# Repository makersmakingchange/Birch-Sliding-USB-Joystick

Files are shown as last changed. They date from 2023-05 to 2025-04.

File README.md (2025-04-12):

# Birch Sliding USB Joystick
The Birch Sliding USB Joystick is a small, proportional joystick that has a sliding motion and can be used for adaptive gaming. It has a small range of motion of ±2mm and requires approximately 115 grams-force to fully deflect. It is low profile, with a height of 2.4 mm with the standard topper. This joystick has interchangable toppers and optional mount adapters. The Birch Sliding USB Joystick has the same joystick mechanism as the Aspen Sliding Joystick, but is the USB version.

The Birch Sliding USB Joystick has a cable with a USB-A connector. It acts as a USB HID gamepad with a single joystick and is compatible with a variety of devices including PC and the USB ports of the Microsoft Xbox Adaptive Controller. The deadzone can be adjusted through a serial interface.

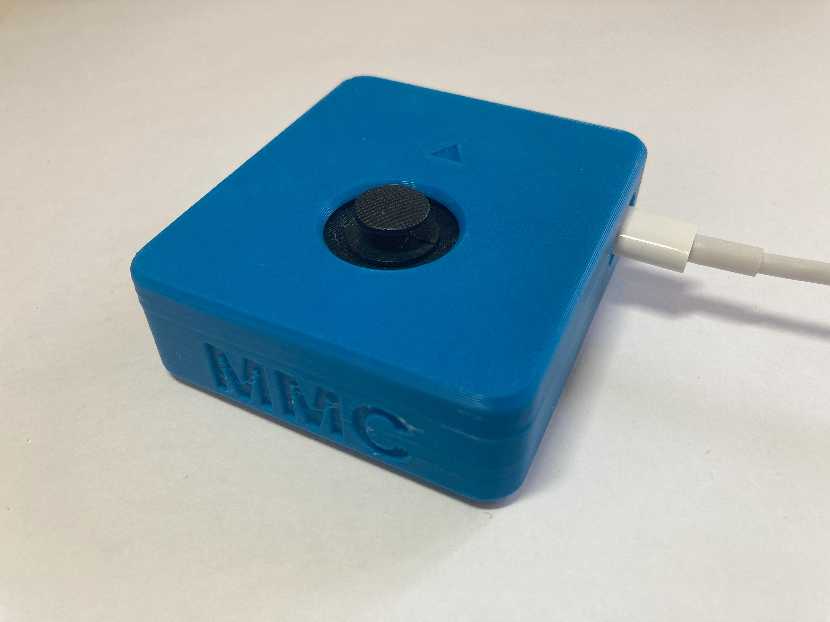
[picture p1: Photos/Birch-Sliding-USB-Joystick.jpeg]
Picture of the Birch Sliding USB Joystick, it is blue and small with MMC written on the side and an arrow on top.


## More info at
- [Makers Making Change Assistive Device Library Listing](https://www.makersmakingchange.com/s/product/birch-sliding-usb-joystick/01tJR0000009357YAA)

## OpenAT Joysticks
This design is part of the [OpenAT Joystick Project](https://github.com/makersmakingchange/OpenAT-Joysticks), a collection of open source designs for digital access and adapted gaming.  

## How to Obtain a Birch Sliding USB Joystick
### 1. Do it Yourself (DIY) or Do it Together (DIT)

This is an open-source assistive technology, so anyone is free to build it. All of the files and instructions required to build the Birch Sliding USB Joystick are contained within this repository. Refer to the Maker Guide below.

### 2. Request a build of this device

If you would like to obtain a Birch Sliding USB Joystick , you may submit a build request through the [MMC Library Page](https://www.makersmakingchange.com/s/product/birch-sliding-usb-joystick/01tJR0000009357YAA). The requestor is responsible for the cost of materials and any shipping.

### 3. How to build this device for someone else

If you have the skills and equipment to build this device, and would like to donate your time to create the switch for someone who needs it, visit the [MMC Maker Wanted](https://makersmakingchange.com/maker-wanted/) section.

## Getting Started

### 1. Verify Joystick Type
The Birch Sliding USB Joystick is a USB joystick that emulates an HID gamepad allowing use either directly with a PC or with the Microsoft Xbox Adaptive Controller (XAC). Verify that this is the type of joystick the user would like. 

If they want an analog joystick with the same sliding motion instead, they should be directed to the [Aspen Sliding Joystick](https://github.com/makersmakingchange/Aspen-Sliding-Joystick). Note: the Aspen Sliding Joystick is compatible with the Sony Access Controller, but the Birch Sliding USB Joystick is not. 

<!---
Other available joysticks can be found through the [Joystick Selection Guide](https://makersmakingchange.com/resource/analog-joystick-selection-guide/)
--->

### 2. Read through the Maker Guide

The [Maker Guide](/Documentation/Birch_Joystick_Maker_Guide.pdf) contains all the neccessary information to build the device.

### 3. Read the Makers Checklist

Use the Makers Checklist in the [Maker Guide](/Documentation/Birch_Joystick_Maker_Guide.pdf) to confirm details and customization options with the user.

### 4. Order the Off-The-Shelf Components

The [Bill of Materials](/Documentation/Birch_Joystick_BOM.csv) lists all of the parts and components required to build the Birch Sliding USB Joystick. 

### 5. Print the 3D Printable components

Print the components needed for the Birch Sliding USB Joystick. Make sure to ask the user if they would like any of the optional prints such as toppers or mount adapters.

All of the files and individual print files can be in the [/Build_Files/3D_Print_Files](/Build_Files/3D_Print_Files/) folder.

### 6. Assemble the Aspen Sliding Joystick

Reference the Assembly Guide section in the [Maker Guide](/Documentation/Birch_Joystick_Maker_Guide.pdf) for the tools and steps required to build the device.

## Files
### Documentation
| Document             | Version | Link | 
|----------------------|---------|------------------------------------------------------------------------------------------|
| Design Rationale     | 1.0     | [Birch_Joystick_Design_Rationale](/Documentation/Birch_Joystick_Design_Rationale.pdf)    | 
| Maker Guide          | 1.0     | [Birch_Joystick_Maker_Guide](/Documentation/Birch_Joystick_Maker_Guide.pdf)     	        | 
| Bill of Materials    | 1.0     | [Birch_Joystick_Bill_of_Materials](/Documentation/Birch_Joystick_BOM.csv)     		    | 
| User Guide           | 1.0     | [Birch_Joystick_User_Guide](/Documentation/Birch_Joystick_User_Guide.pdf)    	    |
| Changelog            | 1.0     | [CHANGES](/CHANGES.txt)     			| 

### Design Files
 - [CAD Files](/Design_Files)

### Build Files
 - [3D Printing Files](/Build_Files/3D_Print_Files)
 - [Firmware](/Build_Files/Software/OpenAT_Joystick_Software_Birch)

## License

Everything needed or used to design, make, test, or prepare the Birch Mini Joystick is licensed under the CERN 2.0 Weakly Reciprocal license <https://ohwr.org/project/cernohl/wikis/Documents/CERN-OHL-version-2> (CERN-OHL-W).

Accompanying material such as instruction manuals, videos, and other copyrightable works that are useful but not necessary to design, make, test, or prepare the Oak Compact Joystick are published under a Creative Commons Attribution-ShareAlike 4.0 license <https://creativecommons.org/licenses/by-sa/4.0/> (CC BY-SA 4.0).

## Attribution

Contributors 
- Josie Versloot, Neil Squire. Hardware and enclosure design, coding, documentation. 
- Tyler Fentie, Neil Squire. Hardware and enclosure design. 
- Milad Hajihassan, Neil Squire. Coding.

The joystick software utilizes the [Adafruit TinyUSB Library for Arduino](https://github.com/adafruit/Adafruit_TinyUSB_Arduino) which is made available under an [MIT license](https://github.com/adafruit/Adafruit_TinyUSB_Arduino/blob/master/LICENSE).

The documentation template was created by Makers Making Change / Neil Squire and is used under a CC BY-SA 4.0 license. It is available at the following link: https://github.com/makersmakingchange/OpenAT-Template

----

<!-- ABOUT MMC START -->
## About Makers Making Change
[Makers Making Change Logo](https://www.makersmakingchange.com/)

Makers Making Change is a program of [Neil Squire](https://www.neilsquire.ca/), a Canadian non-profit that uses technology, knowledge, and passion to empower people with disabilities.

Makers Making Change leverages the capacity of community based Makers, Disability Professionals and Volunteers to develop and deliver affordable Open Source Assistive Technologies.

 - Website: [www.MakersMakingChange.com](https://www.makersmakingchange.com/)
 - GitHub: [makersmakingchange](https://github.com/makersmakingchange)
 - Bluesky: [@makersmakingchange.bsky.social](https://bsky.app/profile/makersmakingchange.bsky.social)
 - Instagram: [@makersmakingchange](https://www.instagram.com/makersmakingchange)
 - Facebook: [makersmakechange](https://www.facebook.com/makersmakechange)
 - LinkedIn: [Neil Squire Society](https://www.linkedin.com/company/neil-squire-society/)
 - Thingiverse: [makersmakingchange](https://www.thingiverse.com/makersmakingchange/about)
 - Printables: [MakersMakingChange](https://www.printables.com/@MakersMakingChange)

### Contact Us
For technical questions, to get involved, or to share your experience we encourage you to [visit our website](https://www.makersmakingchange.com/) or [contact us](https://www.makersmakingchange.com/s/contact).
<!-- ABOUT MMC END -->

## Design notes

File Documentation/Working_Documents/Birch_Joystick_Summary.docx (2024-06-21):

This document is intended to be a summary of a device to make it easier to add to the website.

# Product Information

## Product Name

Birch Sliding USB Joystick

## Device Category

Mark any relevant categories with an “X”:

| Adapted Toys
| Aids for Daily Living (ADL)
| Assistive Switches
| Communication Aids (AAC)
X | Computer Access
| Environmental Controls
X | Gaming
| Keyguard
| Kits
| LipSyncs
| Mounting
X | Recreation and Leisure
| Seating and Positioning
| Switch Interfaces
| Writing Aids

## User Value Statement

If you're looking for a USB joystick with a very small range of motion we'd like to point you to the Birch Sliding USB Joystick.

## Designer

Makers Making Change

# Device Info

## Overview

The Birch Sliding USB Joystick is a small USB joystick that moves in a sliding motion instead of the typical pivoting motion of a joystick or thumbstick. It can be used for adapted gaming, either with the Xbox Adaptive Controller (https://www.xbox.com/en-CA/accessories/controllers/xbox-adaptive-controller) or used directly with PC.

The PSP-style game controller sliding thumbstick joystick has a range of motion of ±2 mm and requires approximately 115 grams-force to fully deflect. A range of toppers are available for this joystick.

## Disability Type

Select one or more disability types and mark with an “X”:

X | Agility / Dexterity
| Arthritis
| Cognitive
| Hearing
| Mobility
| Mobility
| Pain
X | SCI
| Vision
| Other

## Disability Type Description

## For joystick users who require a joystick with a very small range of motion for gaming.

## How To Use

To use the Birch Sliding USB Joystick, first position the joystick for the user, mounting if needed. Then, plug in the USB-C to USB-A cable to both the joystick and the host device, such as the Xbox Adaptive Controller. Wait for the joystick to initialize, then move the joystick like a thumbstick on a standard controller.

For full instructions, please refer to the User Guide. <link>

## Estimated Cost

The estimated material cost of the device for a single build:

| $0 - $10
X | $11 - $25
| $26 - $50
| $51 - $100
| $101 - $250
| $250+

## Attribution

Designed by Neil Squire Society / Makers Making Change

Contributors

- Josie Versloot, Neil Squire. Hardware and enclosure design, coding, documentation.
- Tyler Fentie, Neil Squire. Hardware and enclosure design.
- Milad Hajihassan, Neil Squire. Coding.

The software utilizes the Adafruit TinyUSB Library for Arduino (https://github.com/adafruit/Adafruit_TinyUSB_Arduino) which is made available under an MIT license (https://github.com/adafruit/Adafruit_TinyUSB_Arduino/blob/master/LICENSE).

The documentation template was created by Makers Making Change / Neil Squire and is used under a CC BY-SA 4.0 license. It is available at the following link: https://github.com/makersmakingchange/OpenAT-Template

# Maker Info

## Project Skills

Mark the required project skills with an “X”:

X | 3D Printing
| Custom PCB
X | Electronics
| Laser Cutting
| Mechanics
X | Software
X | Soldering
| Woodworking
| Other

## Skills Description

## This is an intermediate build requiring electronics, mechanics, 3D printing, and using the Arduino IDE.

## Tools Needed

X | 3D Printer
X | Common Hand Tools
| Common Power Tools
| Laser Cutter
X | Soldering Iron
| Specialized Tooling

## Print time (hrs)

4.0

## Assembly time (hrs)

1.0

## Build Instructions

This build consists of a number of off-the-shelf electronic components that are soldered into a protoboard and connected together using wires and solder bridges. The electronics are then assembled into a 3D printed enclosure and the firmware is flashed to the microcontroller using the Arduino IDE.

Detailed step-by-step instructions are available in the Maker Guide <link>.

## Download Link

<Link to direct download of all project files e.g., Github Zip folder>

## Project Link

< Link to GitHub repository>

# License

## License

This repository describes Open Hardware:

- Everything needed or used to design, make, test, or prepare the Birch Sliding USB Joystick is licensed under the CERN 2.0 Weakly Reciprocal license (CERN-OHL-W v2) or later (https://cern.ch/cern-ohl) .
- All software is under the GNU General Public License v3.0 (GPL-3.0) (https://www.gnu.org/licenses/gpl.html).
- Accompanying material such as instruction manuals, videos, and other copyrightable works that are useful but not necessary to design, make, test, or prepare the Birch Sliding USB Joystick are published under a Creative Commons Attribution-ShareAlike 4.0 license (CC BY-SA 4.0) (https://creativecommons.org/licenses/by-sa/4.0/) .

You may redistribute and modify this documentation and make products using it under the terms of the CERN-OHL-W v2 (https://cern.ch/cern-ohl). This documentation is distributed WITHOUT ANY EXPRESS OR IMPLIED WARRANTY, INCLUDING OF MERCHANTABILITY, SATISFACTORY QUALITY AND FITNESS FOR A PARTICULAR PURPOSE. Please see the CERN-OHL-W v2 for applicable conditions.

© 2022 by <Author>. This work is licensed under the CC BY SA 4.0 License: http://creativecommons.org/licenses/by-sa/4.0 Page 1 of 2

V1.0 | MAY 2024 Birch Sliding USB Joystick Summary

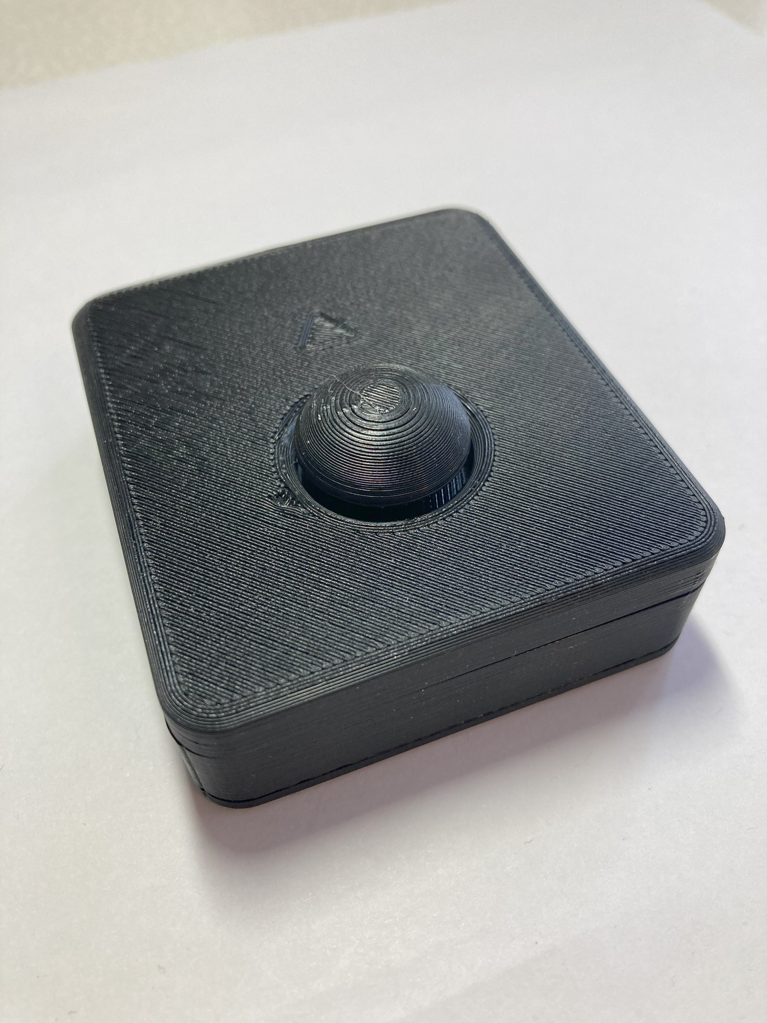
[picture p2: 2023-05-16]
Photos/Birch-Joystick-Medium-Dome-Topper.jpeg

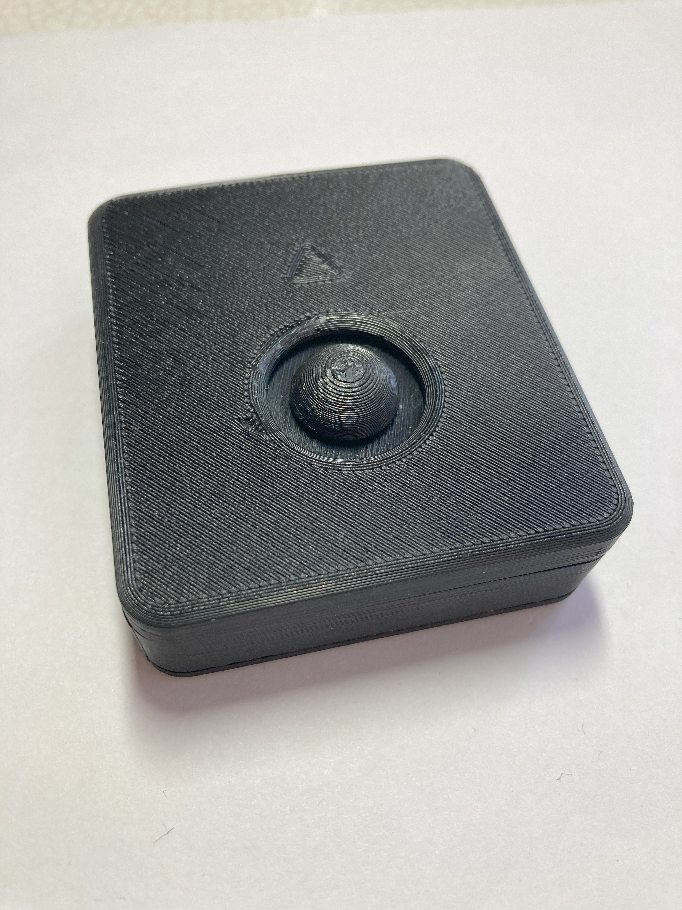
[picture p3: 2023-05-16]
Photos/Birch-Joystick-Small-Dome-Topper.jpeg

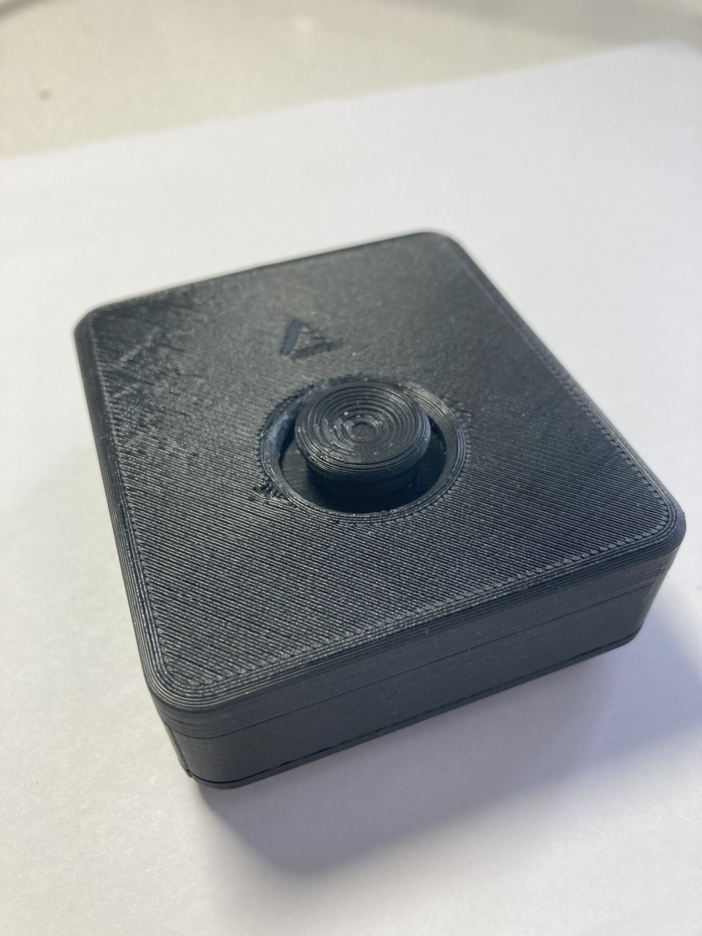
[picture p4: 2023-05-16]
Photos/Birch-Joystick-Concave-Topper.jpeg

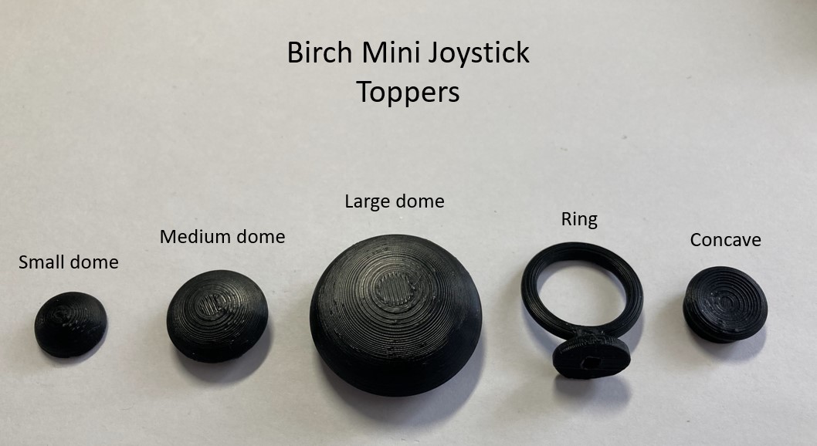
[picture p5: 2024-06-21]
Photos/Birch-Joystick-Toppers-Labelled.jpeg

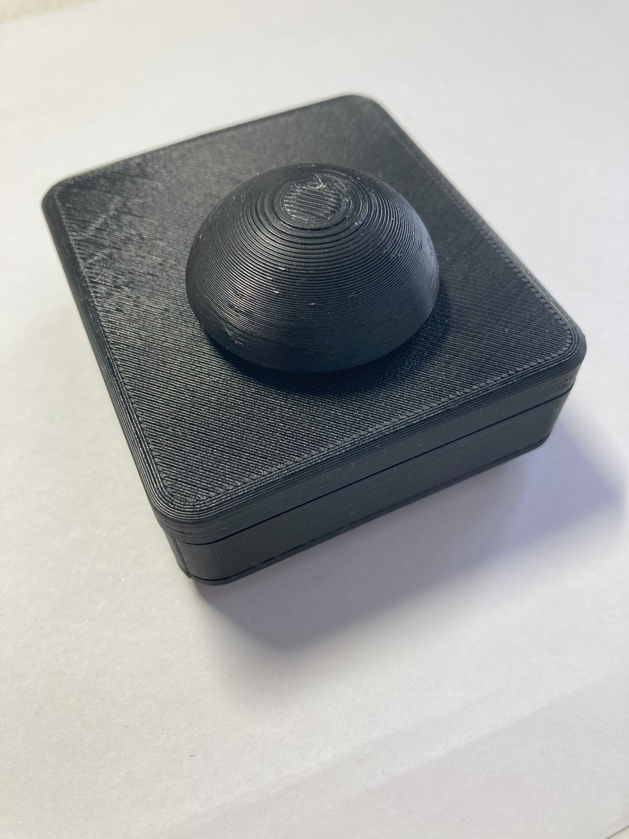
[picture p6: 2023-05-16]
Photos/Birch-Joystick-Large-Dome-Topper.jpeg

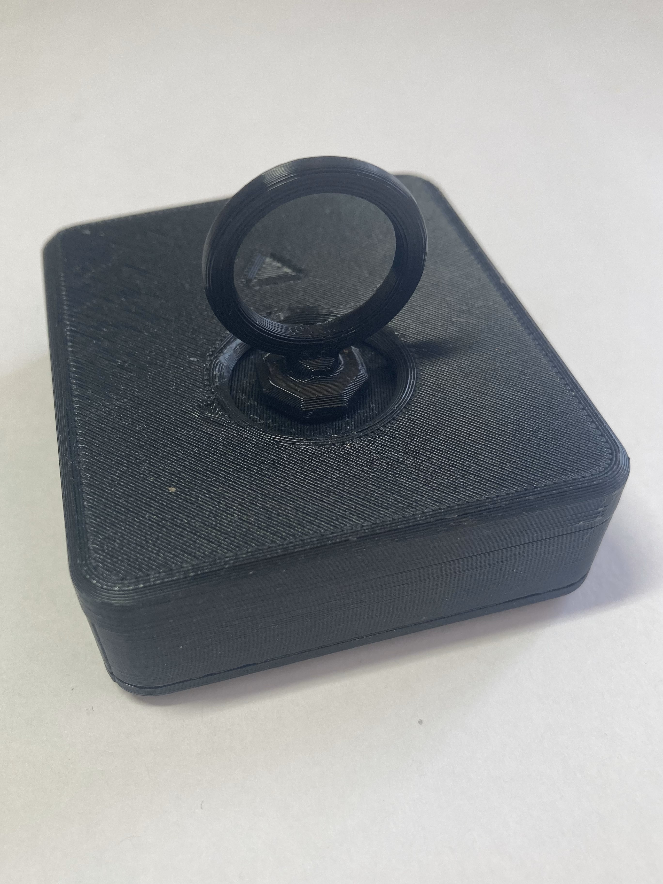
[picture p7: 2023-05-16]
Photos/Birch-Joystick-Ring-Topper.jpeg

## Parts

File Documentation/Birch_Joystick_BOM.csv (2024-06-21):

Birch Sliding USB Joystick |  |  |  |  |  |  |  | Unit Cost | Total Cost | Total Print time (hr) | Total filament (g)
Version: V1.0 |  | Last Updated: 2024-June-18 |  |  |  |  |  | $27.50 | $42.80 | 3.65 | 46.1
Commercial Parts
ID | Part Name | Part Type | QTY | QTY/PKG | $/PKG | PKG QTY | $/Unit | Extended | Total | Link
 | Mini 2-Axis Analog Thumbstick | Electrical | 1 | 1 | $3.87 | 1 | $3.87 | $3.87 | $3.87 | https://www.digikey.ca/en/products/detail/adafruit-industries-llc/2765/6193582
 | Analog Mini Thumbstick Breakout Board | Electrical | 1 | 1 | $2.18 | 1 | $2.18 | $2.18 | $2.18 | https://www.digikey.ca/en/products/detail/adafruit-industries-llc/3246/6193594
 | Universal Proto-board PCB 4cm x 6cm | Electrical | 1 | 3 | $3.63 | 1 | $1.21 | $1.21 | $3.63 | https://www.digikey.ca/en/products/detail/adafruit-industries-llc/4785/13617529
 | SeeedStudio XAIO RP2040 | Electrical | 1 | 1 | $6.80 | 1 | $6.80 | $6.80 | $6.80 | https://www.digikey.ca/en/products/detail/seeed-technology-co-ltd/102010428/14672129
 | 24 AWG Wire, 1 foot | Electrical | 1 | 1 | $0.80 | 1 | $0.80 | $0.80 | $0.80 | https://www.digikey.ca/en/products/detail/cnc-tech/1007-24-1-2000-007-1-TD/17799170
 | M2 x 6 mm Self Tapping Screws | Mechanical | 8 | 1000 | $12.99 | 1 | $0.01 | $0.10 | $12.99 | https://a.co/d/1mQQYbU
 | USB C cable - 6 ft | Electrical | 1 | 1 | $3.28 | 1 | $3.28 | $3.28 | $3.28 | https://www.digikey.ca/en/products/detail/cvilux-usa/DH-20M50053/13177348
 | M3 hex nut x2 | Mechanical | 2 | 1 | $0.28 | 2 | $0.28 | $0.56 | $0.56 | https://www.digikey.ca/en/products/detail/keystone-electronics/4708/4499301
 | (Optional for mount) M3x12mm screw x2 | Mechanical | 0 | 1 | $1.11 | 0 | $1.11 | $- | $- | https://www.digikey.ca/en/products/detail/apm-hexseal/RM3X12MM-2701/2063201
 | (Optional for mount) Tee nut | Mechanical | 0 | 1 | $0.48 | 0 | $0.48 | $- | $- | https://www.homedepot.ca/product/paulin-1-4-inch-20-tee-nuts-4-prong-5-16-inch-barrel-length/1000129429
 | Digikey shipping (if spending less than $100) | Shipping | 1 | 1 | $8.00 | 1 | $8.00 | $8.00 | $8.00
3D Printed Parts ESTIMATED PRICING USING 1KG ROLL COST: |  | $25.00
ID | Part | Material | QTY | Mass (g) / Unit | Time / Unit |  | Print Time (Min) | Estimated Unit Price | Total Price | Link
 | Birch_Enclosure_Bottom | PLA | 1 | 14.9 | 127 |  | 127 | $0.37 | $0.37
 | Birch_Enclosure_Top | PLA | 1 | 10.6 | 74 |  | 74 | $0.27 | $0.27
 | Inner cover disk | PLA | 1 | 0.5 | 4 |  | 4 | $0.01 | $0.01
 | Overlay | PLA | 1 | 1.7 | 14 |  | 14 | $0.04 | $0.04
 | (Optional) Joystick_RAM_B_Mount_Adapter | PLA | 0 | 9.3 | 61 |  | 0 | $0.23 | $-
 | (Optional) Joystick_Camera_Mount | PLA | 0 | 8.5 | 54 |  | 0 | $0.21 | $-
 | (Optional) Topper - small dome | PLA | 0 | 0.6 | 8 |  | 0 | $0.02 | $-
 | (Optional) Topper - medium dome | PLA | 0 | 1.7 | 17 |  | 0 | $0.04 | $-
 | (Optional) Topper - large dome | PLA | 0 | 4.9 | 37 |  | 0 | $0.12 | $-
 | (Optional) Topper - ring | PLA | 0 | 1.5 | 16 |  | 0 | $0.04 | $-
 | (Optional) Topper - concave | PLA | 0 | 1 | 10 |  | 0 | $0.03 | $-
 |  |  |  |  |  |  |  | $- | $-
Custom Printed Circuit Board (PCB)
ID | Part |  | QTY
Tools for Assembly
 | Flush cutters
 | Wire strippers
 | Soldering iron
 | Philips head screw driver
 | 3D printer
 | (Optional for mount adapter) 1/4-20 screw or hex bolt, at least 1/2" long |  |  |  |  |  |  |  |  | https://www.homedepot.ca/product/paulin-1-4-20-x-1-2-inch-hex-head-cap-screw-18-8-stainless-steel-unc/1000142251
Alternatives (if there are other sources for some parts link them below)
ID | Part and description | Part Type | QTY | QTY/PKG | $/PKG | PKG QTY | $/Unit | Extended | Total | Link
 | Universal Proto-board PCB 4cm x 6cm - Amazon | Electrical | 1 | 10 | $11.31 | 1 | $1.13 | $1.13 | $11.31 | https://a.co/d/ftDJjYV
 | Analog Mini Thumbstick Breakout Board - Adafruit | Electrical | 1 | 1 | $1.50 | 1 | $1.50 | $1.50 | $1.50 | https://www.adafruit.com/product/3246
 | Mini 2-Axis Analog Thumbstick | Electrical | 1 | 1 | $2.50 | 1 | $2.50 | $2.50 | $2.50 | https://www.adafruit.com/product/2765
 | 24 Guage wire | Electrical | 1 | 6 | $22.99 | 1 | $3.83 | $3.83 | $22.99 | https://a.co/d/0x1zLnq
 | 24 Guage wire | Electrical | 1 | 3 | $13.99 | 1 | $4.66 | $4.66 | $13.99 | https://a.co/d/e5IVoxq
 | Jumper wire kit - varying lengths | Electrical | 10 | 560 | $18.99 | 1 | $0.03 | $0.34 | $18.99 | https://a.co/d/i4QJhrz
 | 24 Gauge Wire | Electrical | 1 | 3 | $3.95 | 1 | $1.32 | $1.32 | $3.95 | https://www.jameco.com/z/803-3-25-Jameco-Valuepro-Hookup-Wire-24AWG-Solid-Tinned-Copper-Orange-0-052-Inch-OD-PVC-25-Foot-Roll_2300031.html
 | Jumper wire kit - varying lengths | Electrical | 10 | 70 | $6.60 | 1 | $0.09 | $0.94 | $6.60 | https://www.digikey.ca/en/products/detail/global-specialties/WK-3/5231342
 | Tee nuts - 100 pack | Mechanical | 1 | 100 | $14.99 | 1 | $0.15 | $0.15 | $14.99 | https://a.co/d/bvtz0On
 | 2 mm self tapping screws | Mechanical | 8 | 750 | $20.99 | 1 | $0.03 | $0.22 | $20.99 | https://a.co/d/3IzWcJa
 | (Optional for mount) M3 x 10-12mm screws and nuts x2 | Mechanical | 0 | 340 | $22.14 | 0 | $0.07 | $- | $- | https://a.co/d/0B9sK8N
 | USB C cable - 6 ft | Electrical | 1 | 1 | $11.09 | 1 | $11.09 | $11.09 | $11.09 | https://a.co/d/hniaVjO

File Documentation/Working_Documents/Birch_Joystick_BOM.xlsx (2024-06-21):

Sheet: BOM
Birch Sliding USB Joystick |  |  |  |  |  |  |  | Unit Cost | Total Cost | Total Print time (hr) | Total filament (g)
Version: V1.0 |  | Last Updated: 2024-June-18 |  |  |  |  |  | $27.50 | $42.80 | 3.65 | 46.1
Commercial Parts
ID | Part Name | Part Type | QTY | QTY/PKG | $/PKG | PKG QTY | $/Unit | Extended | Total | Link
 | Mini 2-Axis Analog Thumbstick | Electrical | 1 | 1 | $3.87 | 1 | $3.87 | $3.87 | $3.87 | https://www.digikey.ca/en/products/detail/adafruit-industries-llc/2765/6193582
 | Analog Mini Thumbstick Breakout Board | Electrical | 1 | 1 | $2.18 | 1 | $2.18 | $2.18 | $2.18 | https://www.digikey.ca/en/products/detail/adafruit-industries-llc/3246/6193594
 | Universal Proto-board PCB 4cm x 6cm | Electrical | 1 | 3 | $3.63 | 1 | $1.21 | $1.21 | $3.63 | https://www.digikey.ca/en/products/detail/adafruit-industries-llc/4785/13617529
 | SeeedStudio XAIO RP2040 | Electrical | 1 | 1 | $6.80 | 1 | $6.80 | $6.80 | $6.80 | https://www.digikey.ca/en/products/detail/seeed-technology-co-ltd/102010428/14672129
 | 24 AWG Wire, 1 foot | Electrical | 1 | 1 | $0.80 | 1 | $0.80 | $0.80 | $0.80 | https://www.digikey.ca/en/products/detail/cnc-tech/1007-24-1-2000-007-1-TD/17799170
 | M2 x 6 mm Self Tapping Screws | Mechanical | 8 | 1000 | $12.99 | 1 | $0.01 | $0.10 | $12.99 | https://a.co/d/1mQQYbU
 | USB C cable - 6 ft | Electrical | 1 | 1 | $3.28 | 1 | $3.28 | $3.28 | $3.28 | https://www.digikey.ca/en/products/detail/cvilux-usa/DH-20M50053/13177348
 | M3 hex nut x2 | Mechanical | 2 | 1 | $0.28 | 2 | $0.28 | $0.56 | $0.56 | https://www.digikey.ca/en/products/detail/keystone-electronics/4708/4499301
 | (Optional for mount) M3x12mm screw x2 | Mechanical | 0 | 1 | $1.11 | 0 | $1.11 | $0.00 | $0.00 | https://www.digikey.ca/en/products/detail/apm-hexseal/RM3X12MM-2701/2063201
 | (Optional for mount) Tee nut | Mechanical | 0 | 1 | $0.48 | 0 | $0.48 | $0.00 | $0.00 | https://www.homedepot.ca/product/paulin-1-4-inch-20-tee-nuts-4-prong-5-16-inch-barrel-length/1000129429
 | Digikey shipping (if spending less than $100) | Shipping | 1 | 1 | $8.00 | 1 | $8.00 | $8.00 | $8.00
3D Printed Parts ESTIMATED PRICING USING 1KG ROLL COST: |  | $25.00
ID | Part | Material | QTY | Mass (g) / Unit | Time / Unit |  | Print Time (Min) | Estimated Unit Price | Total Price | Link
 | Birch_Enclosure_Bottom | PLA | 1 | 14.9 | 127 |  | 127 | $0.37 | $0.37
 | Birch_Enclosure_Top | PLA | 1 | 10.6 | 74 |  | 74 | $0.27 | $0.27
 | Inner cover disk | PLA | 1 | 0.5 | 4 |  | 4 | $0.01 | $0.01
 | Overlay | PLA | 1 | 1.7 | 14 |  | 14 | $0.04 | $0.04
 | (Optional) Joystick_RAM_B_Mount_Adapter | PLA | 0 | 9.3 | 61 |  | 0 | $0.23 | $0.00
 | (Optional) Joystick_Camera_Mount | PLA | 0 | 8.5 | 54 |  | 0 | $0.21 | $0.00
 | (Optional) Topper - small dome | PLA | 0 | 0.6 | 8 |  | 0 | $0.01 | $0.00
 | (Optional) Topper - medium dome | PLA | 0 | 1.7 | 17 |  | 0 | $0.04 | $0.00
 | (Optional) Topper - large dome | PLA | 0 | 4.9 | 37 |  | 0 | $0.12 | $0.00
 | (Optional) Topper - ring | PLA | 0 | 1.5 | 16 |  | 0 | $0.04 | $0.00
 | (Optional) Topper - concave | PLA | 0 | 1 | 10 |  | 0 | $0.03 | $0.00
 |  |  |  |  |  |  |  | $0.00 | $0.00
Custom Printed Circuit Board (PCB)
ID | Part |  | QTY
Tools for Assembly
 | Flush cutters
 | Wire strippers
 | Soldering iron
 | Philips head screw driver
 | 3D printer
 | (Optional for mount adapter) 1/4-20 screw or hex bolt, at least 1/2" long |  |  |  |  |  |  |  |  | https://www.homedepot.ca/product/paulin-1-4-20-x-1-2-inch-hex-head-cap-screw-18-8-stainless-steel-unc/1000142251
Alternatives (if there are other sources for some parts link them below)
ID | Part and description | Part Type | QTY | QTY/PKG | $/PKG | PKG QTY | $/Unit | Extended | Total | Link
 | Universal Proto-board PCB 4cm x 6cm - Amazon | Electrical | 1 | 10 | $11.31 | 1 | $1.13 | $1.13 | $11.31 | https://a.co/d/ftDJjYV
 | Analog Mini Thumbstick Breakout Board - Adafruit | Electrical | 1 | 1 | $1.50 | 1 | $1.50 | $1.50 | $1.50 | https://www.adafruit.com/product/3246
 | Mini 2-Axis Analog Thumbstick | Electrical | 1 | 1 | $2.50 | 1 | $2.50 | $2.50 | $2.50 | https://www.adafruit.com/product/2765
 | 24 Guage wire | Electrical | 1 | 6 | $22.99 | 1 | $3.83 | $3.83 | $22.99 | https://a.co/d/0x1zLnq
 | 24 Guage wire | Electrical | 1 | 3 | $13.99 | 1 | $4.66 | $4.66 | $13.99 | https://a.co/d/e5IVoxq
 | Jumper wire kit - varying lengths | Electrical | 10 | 560 | $18.99 | 1 | $0.03 | $0.34 | $18.99 | https://a.co/d/i4QJhrz
 | 24 Gauge Wire | Electrical | 1 | 3 | $3.95 | 1 | $1.32 | $1.32 | $3.95 | https://www.jameco.com/z/803-3-25-Jameco-Valuepro-Hookup-Wire-24AWG-Solid-Tinned-Copper-Orange-0-052-Inch-OD-PVC-25-Foot-Roll_2300031.html
 | Jumper wire kit - varying lengths | Electrical | 10 | 70 | $6.60 | 1 | $0.09 | $0.94 | $6.60 | https://www.digikey.ca/en/products/detail/global-specialties/WK-3/5231342
 | Tee nuts - 100 pack | Mechanical | 1 | 100 | $14.99 | 1 | $0.15 | $0.15 | $14.99 | https://a.co/d/bvtz0On
 | 2 mm self tapping screws | Mechanical | 8 | 750 | $20.99 | 1 | $0.03 | $0.22 | $20.99 | https://a.co/d/3IzWcJa
 | (Optional for mount) M3 x 10-12mm screws and nuts x2 | Mechanical | 0 | 340 | $22.14 | 0 | $0.07 | $0.00 | $0.00 | https://a.co/d/0B9sK8N
 | USB C cable - 6 ft | Electrical | 1 | 1 | $11.09 | 1 | $11.09 | $11.09 | $11.09 | https://a.co/d/hniaVjO

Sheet: BOM - Bulk (3)
Birch Sliding USB Joystick |  | (Bulk order: 3) | Number of joysticks |  |  |  |  | Unit Cost (for 1 Joystick) | Cost of materials for 3 joysticks | Total Cost | Maker cost per joystick | Total Print time (hr) | Total filament (g)
Version: V1.0 |  | Last Updated: 2024-June-18 | 3 |  |  |  |  | $22.20 | $66.59 | $79.27 | $26.42 | 4.12 | 50
Commercial Parts
ID | Part Name | Part Type | Unit QTY | QTY | QTY/PKG | $/PKG | PKG QTY | $/Unit | Extended | Total |  | Link
 | Mini 2-Axis Analog Thumbstick | Electrical | 1 | 3 | 1 | $3.87 | 3 | $3.87 | $11.61 | $11.61 |  | https://www.digikey.ca/en/products/detail/adafruit-industries-llc/2765/6193582
 | Analog Mini Thumbstick Breakout Board | Electrical | 1 | 3 | 1 | $2.18 | 3 | $2.18 | $6.54 | $6.54 |  | https://www.digikey.ca/en/products/detail/adafruit-industries-llc/3246/6193594
 | Universal Proto-board PCB 4cm x 6cm | Electrical | 1 | 3 | 3 | $3.63 | 1 | $1.21 | $3.63 | $3.63 |  | https://www.digikey.ca/en/products/detail/adafruit-industries-llc/4785/13617529
 | SeeedStudio XAIO RP2040 | Electrical | 1 | 3 | 1 | $6.80 | 3 | $6.80 | $20.40 | $20.40 |  | https://www.digikey.ca/en/products/detail/seeed-technology-co-ltd/102010428/14672129
 | 24 AWG Wire, 1 foot | Electrical | 1 | 3 | 1 | $0.74 | 3 | $0.74 | $2.22 | $2.22 |  | https://www.digikey.ca/en/products/detail/cnc-tech/1007-24-1-2000-007-1-TD/17799170
 | M2 x 6 mm Self Tapping Screws | Mechanical | 8 | 24 | 1000 | $12.99 | 1 | $0.01 | $0.31 | $12.99 |  | https://a.co/d/1mQQYbU
 | USB C cable - 6 ft | Electrical | 1 | 3 | 1 | $3.28 | 3 | $3.28 | $9.84 | $9.84 |  | https://www.digikey.ca/en/products/detail/cvilux-usa/DH-20M50053/13177348
 | M3 hex nut x2 | Mechanical | 2 | 6 | 1 | $0.28 | 6 | $0.28 | $1.68 | $1.68 |  | https://www.digikey.ca/en/products/detail/keystone-electronics/4708/4499301
 | (Optional for mount) M3x12mm screw x2 | Mechanical | 0 | 0 | 1 | $1.11 | 0 | $1.11 | $0.00 | $0.00 |  | https://www.digikey.ca/en/products/detail/apm-hexseal/RM3X12MM-2701/2063201
 | (Optional for mount) Tee nut | Mechanical | 0 | 0 | 1 | $0.48 | 0 | $0.48 | $0.00 | $0.00 |  | https://www.homedepot.ca/product/paulin-1-4-inch-20-tee-nuts-4-prong-5-16-inch-barrel-length/1000129429
 | Digikey shipping (if spending less than $100) | Shipping | 0.3333333333 | 1 | 1 | $8.00 | 1 | $8.00 | $8.00 | $8.00
3D Printed Parts ESTIMATED PRICING USING 1KG ROLL COST: |  | $25.00
ID | Part | Material | QTY |  | Mass (g) / Unit | Time / Unit |  | Print Time (Min) | Estimated Unit Price | Total Price |  | Link
 | Birch_Enclosure_Bottom | PLA | 1 | 3 | 17.4 | 127 |  | 127 | $0.43 | $1.30
 | Birch_Enclosure_Top | PLA | 1 | 3 | 11.9 | 74 |  | 74 | $0.30 | $0.89
 | Inner cover disk | PLA | 1 | 3 | 0.5 | 4 |  | 4 | $0.01 | $0.04
 | Overlay | PLA | 1 | 3 | 1.7 | 14 |  | 42 | $0.04 | $0.13
 | (Optional) Joystick_RAM_B_Mount_Adapter | PLA | 0 | 0 | 9.3 | 61 |  | 0 | $0.23 | $0.00
 | (Optional) Joystick_Camera_Mount | PLA | 0 | 0 | 8.5 | 54 |  | 0 | $0.21 | $0.00
 | (Optional) Topper - small dome | PLA | 0 | 0 | 0.7 | 8 |  | 0 | $0.02 | $0.00
 | (Optional) Topper - medium dome | PLA | 0 | 0 | 1.8 | 18 |  | 0 | $0.04 | $0.00
 | (Optional) Topper - large dome | PLA | 0 | 0 | 5.5 | 39 |  | 0 | $0.14 | $0.00
 | (Optional) Topper - ring | PLA | 0 | 0 | 1.7 | 16 |  | 0 | $0.04 | $0.00
 | (Optional) Topper - concave | PLA | 0 | 0 | 1 | 11 |  | 0 | $0.03 | $0.00
 |  |  |  |  |  |  |  |  | $0.00 | $0.00
Custom Printed Circuit Board (PCB)
ID | Part |  | QTY
Tools for Assembly
 | Flush cutters
 | Wire strippers
 | Soldering iron
 | Philips head screw driver
 | 3D printer
 | (Optional for mount adapter) 1/4-20 screw or hex bolt, at least 1/2" long |  |  |  |  |  |  |  |  |  |  | https://www.homedepot.ca/product/paulin-1-4-20-x-1-2-inch-hex-head-cap-screw-18-8-stainless-steel-unc/1000142251
Alternatives (if there are other sources for some parts link them below)
ID | Part and description | Part Type | QTY |  | QTY/PKG | $/PKG | PKG QTY | $/Unit | Extended | Total |  | Link
 | Universal Proto-board PCB 4cm x 6cm - Amazon | Electrical | 1 |  | 10 | $11.31 | 1 | $1.13 | $1.13 | $11.31 |  | https://a.co/d/ftDJjYV
 | Analog Mini Thumbstick Breakout Board - Adafruit | Electrical | 1 |  | 1 | $1.50 | 1 | $1.50 | $1.50 | $1.50 |  | https://www.adafruit.com/product/3246
 | Mini 2-Axis Analog Thumbstick | Electrical | 1 |  | 1 | $2.50 | 1 | $2.50 | $2.50 | $2.50 |  | https://www.adafruit.com/product/2765
 | 24 Guage wire | Electrical | 1 |  | 6 | $22.99 | 1 | $3.83 | $3.83 | $22.99 |  | https://a.co/d/0x1zLnq
 | 24 Guage wire | Electrical | 1 |  | 3 | $13.99 | 1 | $4.66 | $4.66 | $13.99 |  | https://a.co/d/e5IVoxq
 | Jumper wire kit - varying lengths | Electrical | 10 |  | 560 | $18.99 | 1 | $0.03 | $0.34 | $18.99 |  | https://a.co/d/i4QJhrz
 | 24 Gauge Wire | Electrical | 1 |  | 3 | $3.95 | 1 | $1.32 | $1.32 | $3.95 |  | https://www.jameco.com/z/803-3-25-Jameco-Valuepro-Hookup-Wire-24AWG-Solid-Tinned-Copper-Orange-0-052-Inch-OD-PVC-25-Foot-Roll_2300031.html
 | Jumper wire kit - varying lengths | Electrical | 10 |  | 70 | $6.60 | 1 | $0.09 | $0.94 | $6.60 |  | https://www.digikey.ca/en/products/detail/global-specialties/WK-3/5231342
 | Tee nuts - 100 pack | Mechanical | 1 |  | 100 | $14.99 | 1 | $0.15 | $0.15 | $14.99 |  | https://a.co/d/bvtz0On
 | 2 mm self tapping screws | Mechanical | 8 |  | 750 | $20.99 | 1 | $0.03 | $0.22 | $20.99 |  | https://a.co/d/3IzWcJa
 | (Optional for mount) M3 x 10-12mm screws and nuts x2 | Mechanical | 0 |  | 340 | $22.14 | 0 | $0.07 | $0.00 | $0.00 |  | https://a.co/d/0B9sK8N

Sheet: BOM - Bulk (6)
Birch Sliding USB Joystick |  | (Bulk order: 6) | Number of joysticks |  |  |  |  | Unit Cost (for 1 Joystick) | Cost for 6 joysticks | Total Cost | Maker cost per joystick | Total Print time (hr) | Total filament (g)
Version: V1.0 |  | Last Updated: 2024-June-18 | 6 |  |  |  |  | $19.53 | $117.19 | $129.55 | $21.59 | 4.82 | 50
Commercial Parts
ID | Part Name | Part Type | Unit QTY | QTY | QTY/PKG | $/PKG | PKG QTY | $/Unit | Extended | Total |  | Link
 | Mini 2-Axis Analog Thumbstick | Electrical | 1 | 6 | 1 | $3.87 | 6 | $3.87 | $23.22 | $23.22 |  | https://www.digikey.ca/en/products/detail/adafruit-industries-llc/2765/6193582
 | Analog Mini Thumbstick Breakout Board | Electrical | 1 | 6 | 1 | $2.18 | 6 | $2.18 | $13.08 | $13.08 |  | https://www.digikey.ca/en/products/detail/adafruit-industries-llc/3246/6193594
 | Universal Proto-board PCB 4cm x 6cm | Electrical | 1 | 6 | 3 | $3.63 | 2 | $1.21 | $7.26 | $7.26 |  | https://www.digikey.ca/en/products/detail/adafruit-industries-llc/4785/13617529
 | SeeedStudio XAIO RP2040 | Electrical | 1 | 6 | 1 | $6.80 | 6 | $6.80 | $40.80 | $40.80 |  | https://www.digikey.ca/en/products/detail/seeed-technology-co-ltd/102010428/14672129
 | 24 AWG Wire, 1 foot | Electrical | 1 | 6 | 1 | $0.74 | 6 | $0.74 | $4.44 | $4.44 |  | https://www.digikey.ca/en/products/detail/cnc-tech/3122-24-1-0500-001-1-TS/16396742
 | M2 x 6 mm Self Tapping Screws | Mechanical | 8 | 48 | 1000 | $12.99 | 1 | $0.01 | $0.62 | $12.99 |  | https://a.co/d/1mQQYbU
 | USB C cable - 6 ft | Electrical | 1 | 6 | 1 | $3.28 | 6 | $3.28 | $19.68 | $19.68 |  | https://www.digikey.ca/en/products/detail/cvilux-usa/DH-20M50053/13177348
 | M3 hex nut x2 | Mechanical | 2 | 12 | 1 | $0.28 | 12 | $0.28 | $3.36 | $3.36 |  | https://www.digikey.ca/en/products/detail/keystone-electronics/4708/4499301
 | (Optional for mount) M3x12mm screw x2 | Mechanical | 0 | 0 | 1 | $1.11 | 0 | $1.11 | $0.00 | $0.00 |  | https://www.digikey.ca/en/products/detail/apm-hexseal/RM3X12MM-2701/2063201
 | (Optional for mount) Tee nut | Mechanical | 0 | 0 | 1 | $0.48 | 0 | $0.48 | $0.00 | $0.00 |  | https://www.homedepot.ca/product/paulin-1-4-inch-20-tee-nuts-4-prong-5-16-inch-barrel-length/1000129429
 | Digikey shipping (if spending less than $100) | Shipping | 0 | 0 | 1 | $8.00 | 0 | $8.00 | $0.00 | $0.00
3D Printed Parts ESTIMATED PRICING USING 1KG ROLL COST: |  | $25.00
ID | Part | Material | QTY |  | Mass (g) / Unit | Time / Unit |  | Print Time (Min) | Estimated Unit Price | Total Price |  | Link
 | Birch_Enclosure_Bottom | PLA | 1 | 6 | 17.4 | 127 |  | 127 | $0.43 | $2.61
 | Birch_Enclosure_Top | PLA | 1 | 6 | 11.9 | 74 |  | 74 | $0.30 | $1.79
 | Inner cover disk | PLA | 1 | 6 | 0.5 | 4 |  | 4 | $0.01 | $0.08
 | Overlay | PLA | 1 | 6 | 1.7 | 14 |  | 84 | $0.04 | $0.26
 | (Optional) Joystick_RAM_B_Mount_Adapter | PLA | 0 | 0 | 9.3 | 61 |  | 0 | $0.23 | $0.00
 | (Optional) Joystick_Camera_Mount | PLA | 0 | 0 | 8.5 | 54 |  | 0 | $0.21 | $0.00
 | (Optional) Topper - small dome | PLA | 0 | 0 | 0.7 | 8 |  | 0 | $0.02 | $0.00
 | (Optional) Topper - medium dome | PLA | 0 | 0 | 1.8 | 18 |  | 0 | $0.04 | $0.00
 | (Optional) Topper - large dome | PLA | 0 | 0 | 5.5 | 39 |  | 0 | $0.14 | $0.00
 | (Optional) Topper - ring | PLA | 0 | 0 | 1.7 | 16 |  | 0 | $0.04 | $0.00
 | (Optional) Topper - concave | PLA | 0 | 0 | 1 | 11 |  | 0 | $0.03 | $0.00
 |  |  |  |  |  |  |  |  | $0.00 | $0.00
Custom Printed Circuit Board (PCB)
ID | Part |  | QTY
Tools for Assembly
 | Flush cutters
 | Wire strippers
 | Soldering iron
 | Philips head screw driver
 | 3D printer
 | (Optional for mount adapter) 1/4-20 screw or hex bolt, at least 1/2" long |  |  |  |  |  |  |  |  |  |  | https://www.homedepot.ca/product/paulin-1-4-20-x-1-2-inch-hex-head-cap-screw-18-8-stainless-steel-unc/1000142251
Alternatives (if there are other sources for some parts link them below)
ID | Part and description | Part Type | QTY |  | QTY/PKG | $/PKG | PKG QTY | $/Unit | Extended | Total |  | Link
 | Universal Proto-board PCB 4cm x 6cm - Amazon | Electrical | 1 |  | 10 | $11.31 | 1 | $1.13 | $1.13 | $11.31 |  | https://a.co/d/ftDJjYV
 | Analog Mini Thumbstick Breakout Board - Adafruit | Electrical | 1 |  | 1 | $1.50 | 1 | $1.50 | $1.50 | $1.50 |  | https://www.adafruit.com/product/3246
 | Mini 2-Axis Analog Thumbstick | Electrical | 1 |  | 1 | $2.50 | 1 | $2.50 | $2.50 | $2.50 |  | https://www.adafruit.com/product/2765
 | 24 Guage wire | Electrical | 1 |  | 6 | $22.99 | 1 | $3.83 | $3.83 | $22.99 |  | https://a.co/d/0x1zLnq
 | 24 Guage wire | Electrical | 1 |  | 3 | $13.99 | 1 | $4.66 | $4.66 | $13.99 |  | https://a.co/d/e5IVoxq
 | Jumper wire kit - varying lengths | Electrical | 10 |  | 560 | $18.99 | 1 | $0.03 | $0.34 | $18.99 |  | https://a.co/d/i4QJhrz
 | 24 Gauge Wire | Electrical | 1 |  | 3 | $3.95 | 1 | $1.32 | $1.32 | $3.95 |  | https://www.jameco.com/z/803-3-25-Jameco-Valuepro-Hookup-Wire-24AWG-Solid-Tinned-Copper-Orange-0-052-Inch-OD-PVC-25-Foot-Roll_2300031.html
 | Jumper wire kit - varying lengths | Electrical | 10 |  | 70 | $6.60 | 1 | $0.09 | $0.94 | $6.60 |  | https://www.digikey.ca/en/products/detail/global-specialties/WK-3/5231342
 | Tee nuts - 100 pack | Mechanical | 1 |  | 100 | $14.99 | 1 | $0.15 | $0.15 | $14.99 |  | https://a.co/d/bvtz0On
 | 2 mm self tapping screws | Mechanical | 8 |  | 750 | $20.99 | 1 | $0.03 | $0.22 | $20.99 |  | https://a.co/d/3IzWcJa

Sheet: BOM - Bulk (10)
Birch Sliding USB Joystick |  | (Bulk order: 10) | Number of joysticks |  |  |  |  | Unit Cost (for 1 Joystick) | Cost for 10 joysticks | Total Cost | Maker cost per joystick | Total Print time (hr) | Total filament (g)
Version: V1.0 |  | Last Updated: 2024-June-18 | 10 |  |  |  |  | $19.84 | $198.38 | $212.75 | $21.28 | 5.75 | 50
Commercial Parts
ID | Part Name | Part Type | Unit QTY | QTY | QTY/PKG | $/PKG | PKG QTY | $/Unit | Extended | Total |  | Link
 | Mini 2-Axis Analog Thumbstick | Electrical | 1 | 10 | 1 | $3.87 | 10 | $3.87 | $38.70 | $38.70 |  | https://www.digikey.ca/en/products/detail/adafruit-industries-llc/2765/6193582
 | Analog Mini Thumbstick Breakout Board | Electrical | 1 | 10 | 1 | $2.18 | 10 | $2.18 | $21.80 | $21.80 |  | https://www.digikey.ca/en/products/detail/adafruit-industries-llc/3246/6193594
 | Universal Proto-board PCB 4cm x 6cm | Electrical | 1 | 10 | 3 | $3.63 | 4 | $1.21 | $12.10 | $14.52 |  | https://www.digikey.ca/en/products/detail/adafruit-industries-llc/4785/13617529
 | SeeedStudio XAIO RP2040 | Electrical | 1 | 10 | 1 | $6.80 | 10 | $6.80 | $68.00 | $68.00 |  | https://www.digikey.ca/en/products/detail/seeed-technology-co-ltd/102010428/14672129
 | 24 AWG Wire, 1 foot | Electrical | 1 | 10 | 1 | $0.68 | 10 | $0.68 | $6.77 | $6.77 |  | https://www.digikey.ca/en/products/detail/cnc-tech/3122-24-1-0500-001-1-TS/16396742
 | M2 x 6 mm Self Tapping Screws | Mechanical | 8 | 80 | 1000 | $12.99 | 1 | $0.01 | $1.04 | $12.99 |  | https://a.co/d/1mQQYbU
 | USB C cable - 6 ft | Electrical | 1 | 10 | 1 | $2.85 | 10 | $2.85 | $28.50 | $28.50 |  | https://www.digikey.ca/en/products/detail/cvilux-usa/DH-20M50053/13177348
 | M3 hex nut x2 | Mechanical | 2 | 20 | 1 | $0.28 | 20 | $0.28 | $5.60 | $5.60 |  | https://www.digikey.ca/en/products/detail/keystone-electronics/4708/4499301
 | (Optional for mount) M3x12mm screw x2 | Mechanical | 0 | 0 | 1 | $1.11 | 0 | $1.11 | $0.00 | $0.00 |  | https://www.digikey.ca/en/products/detail/apm-hexseal/RM3X12MM-2701/2063201
 | (Optional for mount) Tee nut | Mechanical | 0 | 0 | 1 | $0.48 | 0 | $0.48 | $0.00 | $0.00 |  | https://www.homedepot.ca/product/paulin-1-4-inch-20-tee-nuts-4-prong-5-16-inch-barrel-length/1000129429
 | Digikey shipping (if spending less than $100) | Shipping | 0.1 | 1 | 1 | $8.00 | 1 | $8.00 | $8.00 | $8.00
3D Printed Parts ESTIMATED PRICING USING 1KG ROLL COST: |  | $25.00
ID | Part | Material | QTY |  | Mass (g) / Unit | Time / Unit |  | Print Time (Min) | Estimated Unit Price | Total Price |  | Link
 | Birch_Enclosure_Bottom | PLA | 1 | 10 | 17.4 | 127 |  | 127 | $0.43 | $4.35
 | Birch_Enclosure_Top | PLA | 1 | 10 | 11.9 | 74 |  | 74 | $0.30 | $2.98
 | Inner cover disk | PLA | 1 | 10 | 0.5 | 4 |  | 4 | $0.01 | $0.12
 | Overlay | PLA | 1 | 10 | 1.7 | 14 |  | 140 | $0.04 | $0.42
 | (Optional) Joystick_RAM_B_Mount_Adapter | PLA | 0 | 0 | 9.3 | 61 |  | 0 | $0.23 | $0.00
 | (Optional) Joystick_Camera_Mount | PLA | 0 | 0 | 8.5 | 54 |  | 0 | $0.21 | $0.00
 | (Optional) Topper - small dome | PLA | 0 | 0 | 0.7 | 8 |  | 0 | $0.02 | $0.00
 | (Optional) Topper - medium dome | PLA | 0 | 0 | 1.8 | 18 |  | 0 | $0.04 | $0.00
 | (Optional) Topper - large dome | PLA | 0 | 0 | 5.5 | 39 |  | 0 | $0.14 | $0.00
 | (Optional) Topper - ring | PLA | 0 | 0 | 1.7 | 16 |  | 0 | $0.04 | $0.00
 | (Optional) Topper - concave | PLA | 0 | 0 | 1 | 11 |  | 0 | $0.03 | $0.00
 |  |  |  |  |  |  |  |  | $0.00 | $0.00
Custom Printed Circuit Board (PCB)
ID | Part |  | QTY
Tools for Assembly
 | Flush cutters
 | Wire strippers
 | Soldering iron
 | Philips head screw driver
 | 3D printer
 | (Optional for mount adapter) 1/4-20 screw or hex bolt, at least 1/2" long |  |  |  |  |  |  |  |  |  |  | https://www.homedepot.ca/product/paulin-1-4-20-x-1-2-inch-hex-head-cap-screw-18-8-stainless-steel-unc/1000142251
Alternatives (if there are other sources for some parts link them below)
ID | Part and description | Part Type | QTY |  | QTY/PKG | $/PKG | PKG QTY | $/Unit | Extended | Total |  | Link
 | Universal Proto-board PCB 4cm x 6cm - Amazon | Electrical | 1 |  | 10 | $11.31 | 1 | $1.13 | $1.13 | $11.31 |  | https://a.co/d/ftDJjYV
 | Analog Mini Thumbstick Breakout Board - Adafruit | Electrical | 1 |  | 1 | $1.50 | 1 | $1.50 | $1.50 | $1.50 |  | https://www.adafruit.com/product/3246
 | Mini 2-Axis Analog Thumbstick | Electrical | 1 |  | 1 | $2.50 | 1 | $2.50 | $2.50 | $2.50 |  | https://www.adafruit.com/product/2765
 | 24 Guage wire | Electrical | 1 |  | 6 | $22.99 | 1 | $3.83 | $3.83 | $22.99 |  | https://a.co/d/0x1zLnq
 | 24 Guage wire | Electrical | 1 |  | 3 | $13.99 | 1 | $4.66 | $4.66 | $13.99 |  | https://a.co/d/e5IVoxq
 | Jumper wire kit - varying lengths | Electrical | 10 |  | 560 | $18.99 | 1 | $0.03 | $0.34 | $18.99 |  | https://a.co/d/i4QJhrz
 | 24 Gauge Wire | Electrical | 1 |  | 3 | $3.95 | 1 | $1.32 | $1.32 | $3.95 |  | https://www.jameco.com/z/803-3-25-Jameco-Valuepro-Hookup-Wire-24AWG-Solid-Tinned-Copper-Orange-0-052-Inch-OD-PVC-25-Foot-Roll_2300031.html
 | Jumper wire kit - varying lengths | Electrical | 10 |  | 70 | $6.60 | 1 | $0.09 | $0.94 | $6.60 |  | https://www.digikey.ca/en/products/detail/global-specialties/WK-3/5231342
 | Tee nuts - 100 pack | Mechanical | 1 |  | 100 | $14.99 | 1 | $0.15 | $0.15 | $14.99 |  | https://a.co/d/bvtz0On
 | 2 mm self tapping screws | Mechanical | 8 |  | 750 | $20.99 | 1 | $0.03 | $0.22 | $20.99 |  | https://a.co/d/3IzWcJa

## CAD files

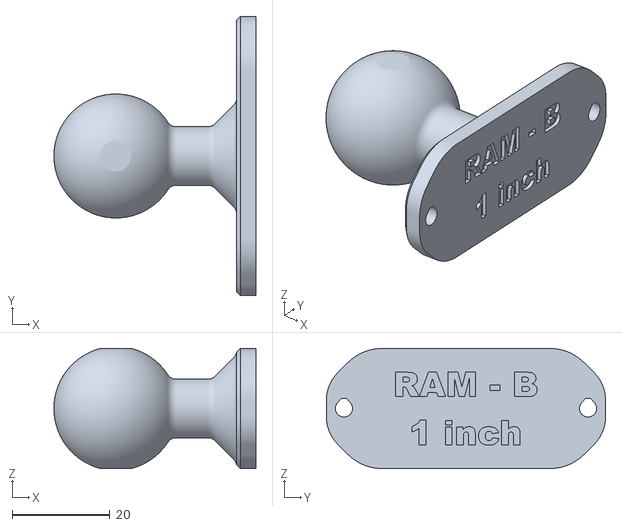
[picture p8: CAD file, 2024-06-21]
Build_Files/3D_Print_Files/Joystick_RAM_B_Mount_Adapter.stl
41.4 x 57.2 x 24.6

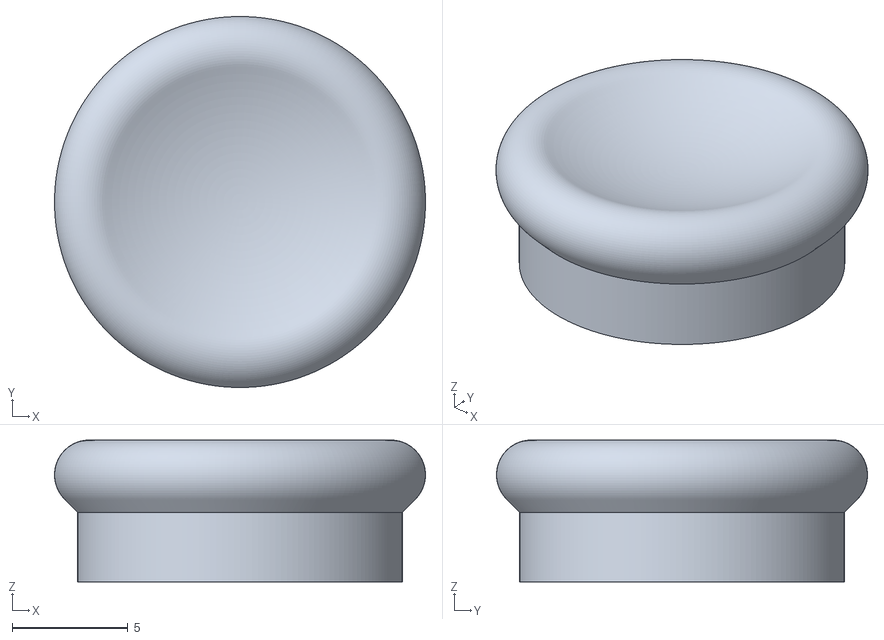
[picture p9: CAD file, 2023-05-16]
Build_Files/3D_Print_Files/Toppers/Sliding_Topper_Concave.stl
16.0 x 16.0 x 6.12

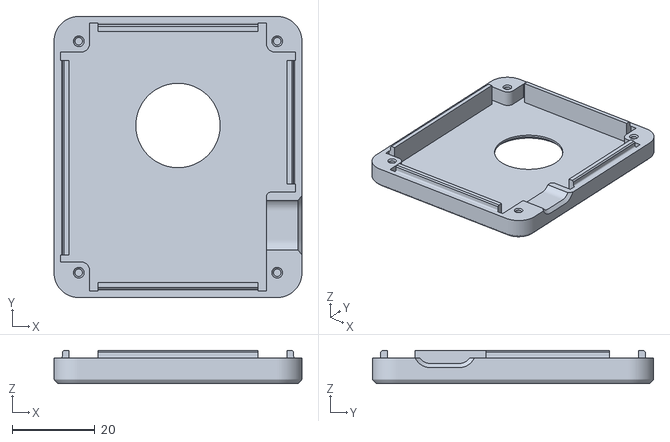
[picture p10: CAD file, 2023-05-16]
Build_Files/3D_Print_Files/Birch_Enclosure_Top.stl
60.0 x 68.0 x 8.10

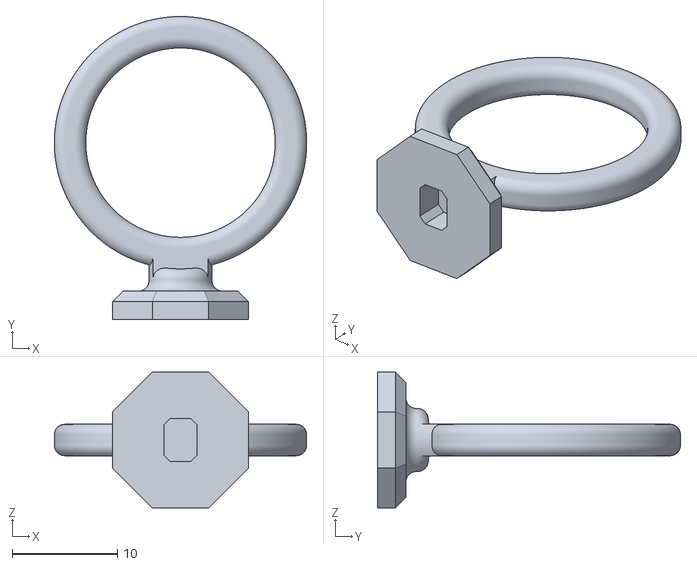
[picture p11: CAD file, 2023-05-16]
Build_Files/3D_Print_Files/Toppers/Sliding_Topper_Ring.stl
24.0 x 28.8 x 12.9

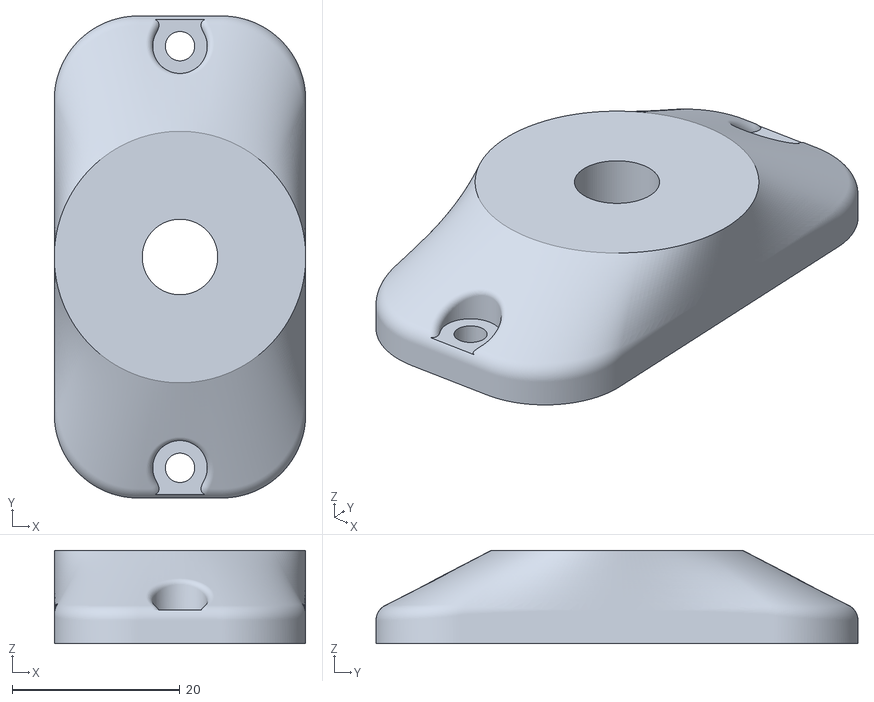
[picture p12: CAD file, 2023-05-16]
Build_Files/3D_Print_Files/Joystick_Camera_Mount_Adapter.stl
30.0 x 57.5 x 11.1

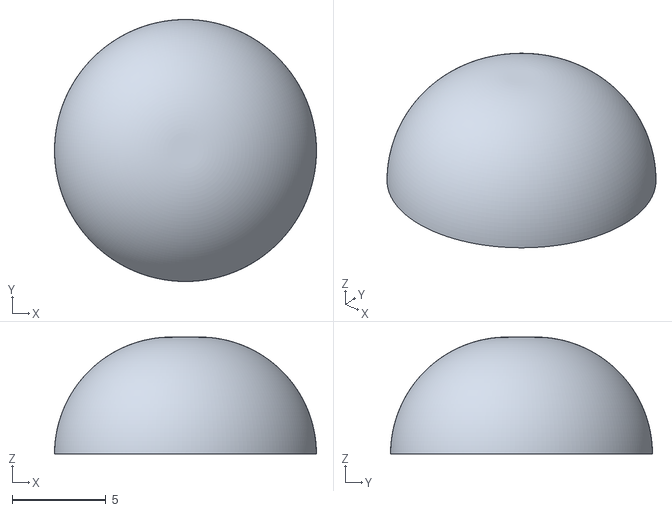
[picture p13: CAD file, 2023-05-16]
Build_Files/3D_Print_Files/Toppers/Sliding_Topper_Small_dome.stl
14.0 x 14.0 x 6.25

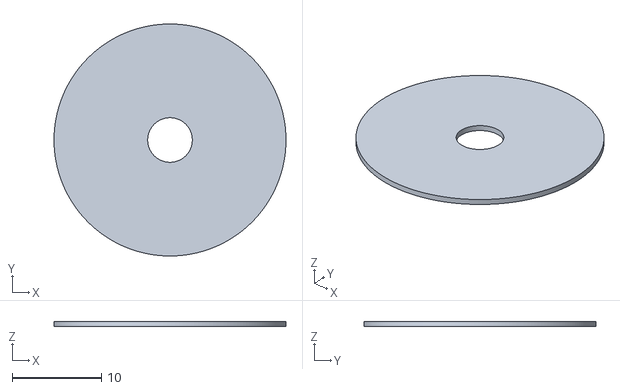
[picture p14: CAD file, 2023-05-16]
Build_Files/3D_Print_Files/Inner_cover_disk.stl
26.0 x 26.0 x 0.6

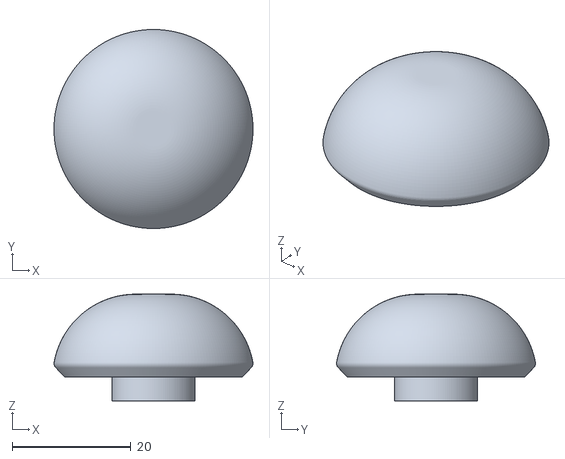
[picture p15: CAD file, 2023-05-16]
Build_Files/3D_Print_Files/Toppers/Sliding_Topper_Large_dome.stl
33.6 x 33.6 x 18.0

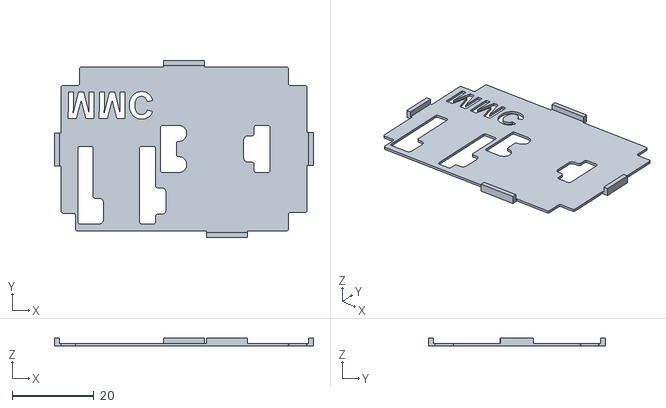
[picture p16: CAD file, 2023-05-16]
Build_Files/3D_Print_Files/Birch_Overlay.stl
63.2 x 43.2 x 2.00

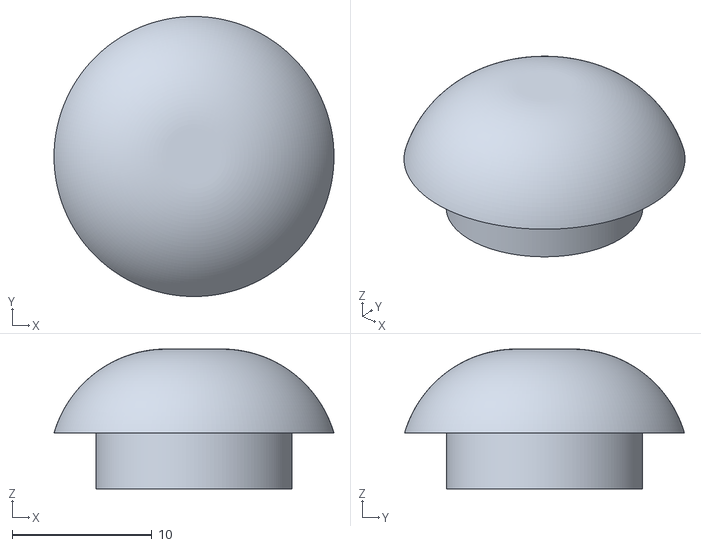
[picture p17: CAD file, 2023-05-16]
Build_Files/3D_Print_Files/Toppers/Sliding_Topper_Medium_dome.stl
20.0 x 20.0 x 10.0

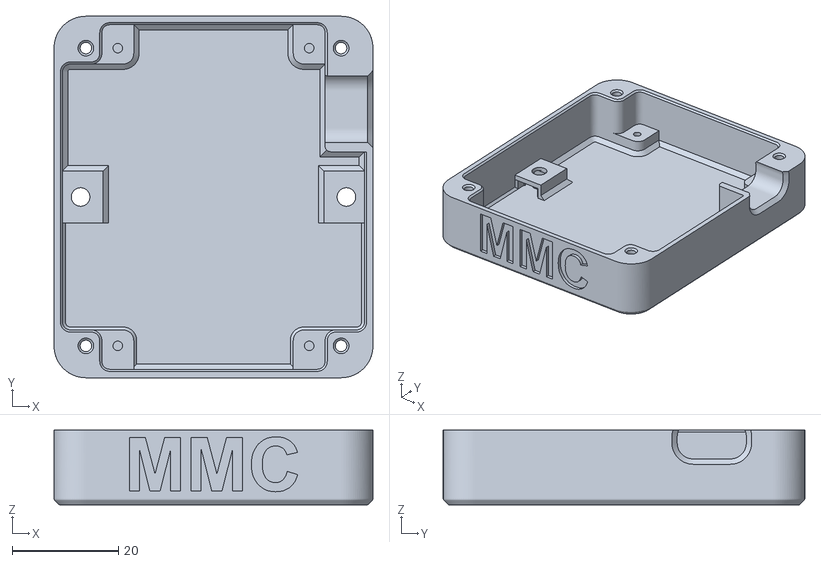
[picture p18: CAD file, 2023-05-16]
Build_Files/3D_Print_Files/Birch_Enclosure_Bottom.stl
60.0 x 68.0 x 14.1

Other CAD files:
Design_Files/Birch_Mini_Joystick_Housing_Bottom v23.f3d
Design_Files/Birch_Mini_Joystick_Housing_Top v46.f3d
Design_Files/Inner cover disk v6.f3d
Design_Files/Joystick RAM Mount Adapter v5.f3d
Design_Files/Joystick_Camera_Mount Narrow v3.f3d
Design_Files/Joystick_Camera_Mount v9.f3d
Design_Files/Overlay v8.f3d
Design_Files/Topper - concave v2.f3d
Design_Files/Topper - large dome v3.f3d
Design_Files/Topper - medium dome v4.f3d
Design_Files/Topper - ring v5.f3d
Design_Files/Topper - small dome v8.f3d

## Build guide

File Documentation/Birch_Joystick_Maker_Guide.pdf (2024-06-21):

V1.0 | JUNE 2024

## Birch Sliding USB Joystick

## MAKER GUIDE

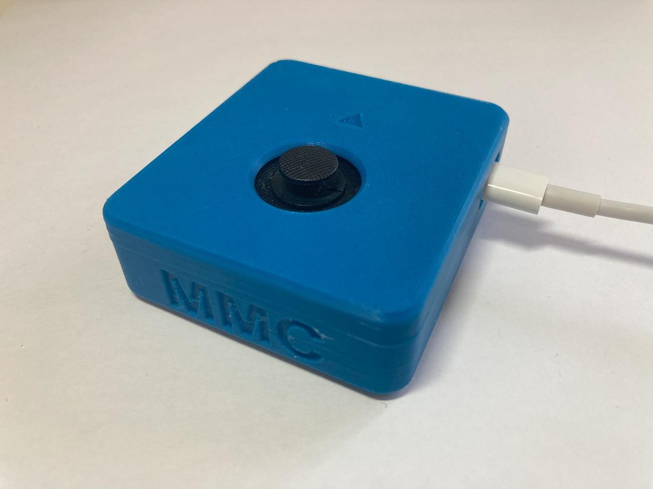
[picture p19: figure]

© 2023 by Neil Squire Society. (https://www.neilsquire.ca/) This work is licensed under the CC BY SA 4.0 License: http://creativecommons.org/licenses/by-sa/4.0
Files available at https://github.com/makersmakingchange/Birch-Mini-Joystick | Page 1 of 31

### Overview

This document contains the necessary information to build the Birch Sliding USB Joystick, including a customization guide, 3D printing guide, assembly guide, and instructions to test the finished joystick.

## MAKER GUIDE

Files available at https://github.com/makersmakingchange/Birch-Mini-Joystick | Page 2 of 31

### Contents

Overview | 1
Maker Checklist | 4
Maker To Do List | 4
Items to Give to User | 4
Tool List | 5
Customization Guide | 5
Joystick | 5
Toppers | 5
Mounting | 5
3D Printing Guide | 6
3D Printing Summary | 6
3D Printing Settings | 6
Joystick Enclosure - REQUIRED | 6
Toppers and Mount Adapters* - OPTIONAL | 6
Post-Processing | 7
Customization Options | 7
Examples of Quality Prints | 7
Birch_Enclosure_Bottom | 7
Birch_Enclosure_Top | 8
Inner_Cover_Disk | 8
Overlay | 9
Joystick Camera Mount Adapter | 9
Joystick toppers | 9
Assembly Guide | 10
Required Components | 10
Required Tools | 11
Required Personal Protective Equipment (PPE) | 11
Joystick Assembly | 12
Step 1: Position the overlay | 12

## MAKER GUIDE

Files available at https://github.com/makersmakingchange/Birch-Mini-Joystick | Page 3 of 31
Step 2: Position microcontroller headers | 12
Step 3: Solder two header pins to board | 13
Step 4: Solder remaining header pins to board | 13
Step 5: Solder joystick to breakout board | 14
Step 6: Position joystick headers | 14
Step 7: Solder two header pins to board | 15
Step 8: Solder remaining header pins to board | 15
Step 9: Remove joystick and microcontroller | 16
Wiring | 16
Step 10: Position first wire | 17
Step 11: Solder first wire | 17
Step 12: Position and solder second wire | 18
Step 13: Position and solder third wire | 18
Step 14: Position and solder fourth wire | 19
Step 15: Trim pins on the bottom of the board | 19
Step 16: Trim excess wire on the top of the board | 20
Step 17: Position microcontroller and joystick | 21
Step 17: Solder pins on microcontroller and joystick breakout board | 21
Step 18: Insert M3 nuts | 22
Step 19: Screw protoboard into enclosure bottom | 22
Step 20: Position inner disk | 23
Step 21: Position enclosure top | 23
Step 22: Screw enclosure together | 24
Step 23: Plug in USB-C cable | 24
Programming instructions | 25
Testing | 28

## MAKER GUIDE

Files available at https://github.com/makersmakingchange/Birch-Mini-Joystick | Page 4 of 31

### Maker Checklist

This list provides an overview of the steps required to build and deliver the device.

### Maker To Do List

Read through the Maker Guide to become familiar with required components, tools, supplies, safety gear, and overall assembly steps.
Verify the user wants a USB joystick and ask the user if they would if they have a device to connect the joystick to.
- Xbox Adaptive Controller (https://www.xbox.com/en-CA/accessories/controllers/xbox-adaptive-controller)
- PC (for gaming)
Ask the user if they would like any joystick toppers.
Ask the user if they would like a specific mounting solution.
Talk to User about customization options (e.g., colour, any special requests, etc.). Order hardware components.
3D print all 3D printed components.
Gather tools, supplies, and safety equipment.
Assemble the device.
Test device.
Print “User Guide”

### Items to Give to User

Assembled, tested device
USB cable
Any joystick toppers if requested. Any mount adapters if requested. “User Guide”

## MAKER GUIDE

Files available at https://github.com/makersmakingchange/Birch-Mini-Joystick | Page 5 of 31

### Tool List

- Flush Cutters
- Wire Strippers
- Soldering Iron
- Philips Head Screwdriver

### Customization Guide

### Joystick

The enclosure can be printed in the user’s desired colour(s). Colour swaps can be done to further customize the joystick and make the forward arrow on the top stand out more.

### Toppers

3D printed joystick toppers can be added to the joystick. Current topper type include the small dome, medium dome, large dome, ring, and concave (shown left to right). These toppers can also be modified through the original design files.

### Mounting

Mount adapters can be added for custom mounting solutions. Current mounting options include nonslip pads, hook and loop fastener, a ¼-20 camera mount adapter, and a RAM-B mount adapter.

## MAKER GUIDE

Files available at https://github.com/makersmakingchange/Birch-Mini-Joystick | Page 6 of 31

### 3D Printing Guide

### 3D Printing Summary

Metrics | Joystick housing only (No optional prints) | All files including optional prints
Total Print Time (h:min) | 3:11 | 5:33
Total Number of Components | 4 | 10
Typical Total Mass (g) | 27.7 | 45.9
Typical Number of Print Setups | 1 | 1

### 3D Printing Settings

Joystick Enclosure - REQUIRED
Print File Name | Qty | Total Print Time (hr:min) | Mass (g) | Infill (%) | Support (Y/N) | Layer Height/ Nozzle Diameter(mm) | Notes (orientation, special settings, etc.)
Birch_Enclosure_ Bottom | 1 | 1:46 | 14.9 | 20 | N | 0.2/0.4
Birch_Enclosure_Top | 1 | 1:07 | 10.6 | 20 | N | 0.2/0.4
Inner_cover_disk | 1 | 0:04 | 0.5 | 20 | N | 0.2/0.4
Overlay | 1 | 0:14 | 1.7 | 20 | N | 0.2/0.4

Toppers and Mount Adapters* - OPTIONAL
Print File Name | Qty | Total Print Time (hr:min) | Mass (g) | Infill (%) | Support (Y/N) | Layer Height/ Nozzle Diameter(mm) | Notes (orientation, special settings, etc.)
Joystick_Camera_ Mount_Adapter | 1 | 0:54 | 8.5 | 20 | Y | 0.2/0.4
Joystick_RAM_B_ Mount_Adapter | 1 | 1:01 | 9.3 | 20 | Y | 0.2/0.4
Birch_Topper_Small_ dome | 1 | 0:08 | 0.6 | 20 | N | 0.2/0.4
Birch_Topper_ Medium_dome | 1 | 0:17 | 1.7 | 20 | Y | 0.2/0.4
Birch_Topper_Large_ dome | 1 | 0:37 | 4.9 | 20 | Y | 0.2/0.4
Birch_Topper_Ring | 1 | 0:16 | 1.5 | 20 | Y | 0.2/0.4 | Print with ring parallel to print bed
Birch_Topper_ Concave | 1 | 0:10 | 1.0 | 20 | N | 0.2/0.4

## MAKER GUIDE

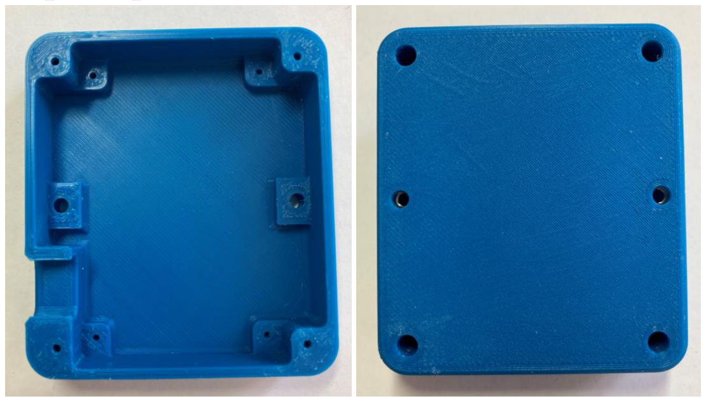
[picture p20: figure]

Files available at https://github.com/makersmakingchange/Birch-Mini-Joystick | Page 7 of 31

### Post-Processing

- Remove any bumps or zits from the surface where the enclosure meets the lid.
- Remove any bumps or zits from both surfaces of the inner cover disk. If any binding occurs between the joystick and the inner cover disk when assembling, sand down this part.
- Remove any supports from camera mount or toppers if printed.

### Customization Options

- Joystick housing can be printed in multiple colours.
- The joystick camera mount adapter is an optional add-on for mounting using ¼-20 threads
- The optional topper prints can customize the joystick for different users

### Examples of Quality Prints

Birch_Enclosure_Bottom

## MAKER GUIDE

Files available at https://github.com/makersmakingchange/Birch-Mini-Joystick | Page 8 of 31

Birch_Enclosure_Top

Inner_Cover_Disk

## MAKER GUIDE

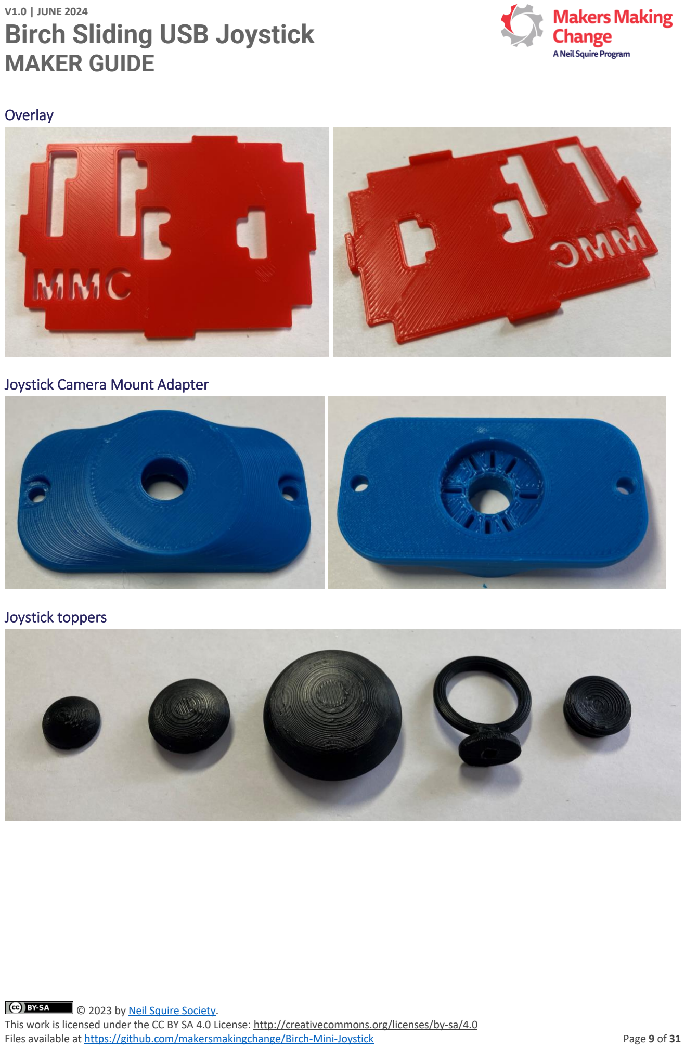
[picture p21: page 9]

Files available at https://github.com/makersmakingchange/Birch-Mini-Joystick | Page 9 of 31

Overlay

Joystick Camera Mount Adapter

Joystick toppers

## MAKER GUIDE

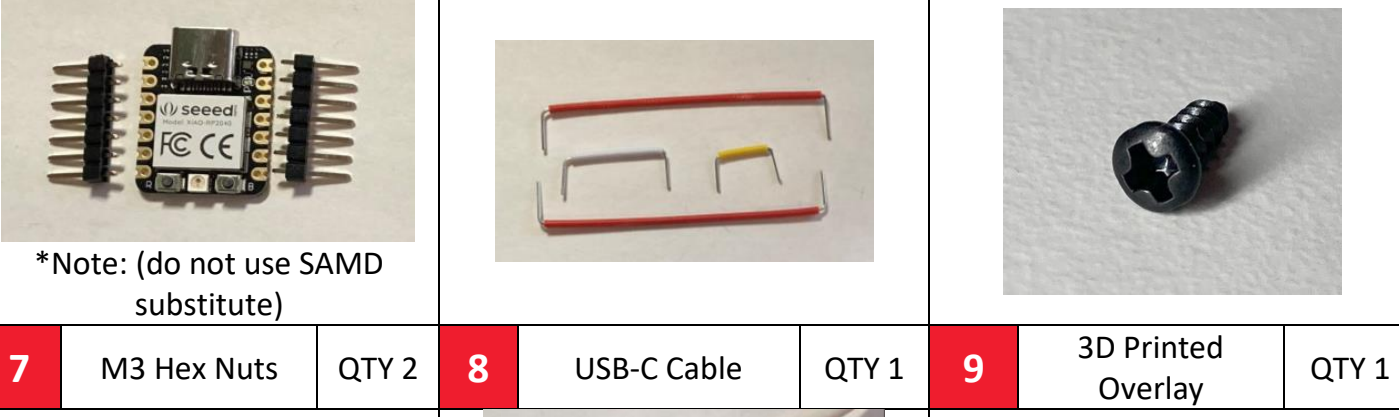
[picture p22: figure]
*Note: (do not use SAMD substitute); M3 Hex Nuts; QTY 2; USB-C Cable; QTY 1; 3D Printed Overlay

Files available at https://github.com/makersmakingchange/Birch-Mini-Joystick | Page 10 of 31

### Assembly Guide

### Required Components

1

Mini 2-Axis
Analog
Thumbstick

QTY 1 2

Mini Thumbstick
Breakout Board
with included 8
pin male header

QTY 1 3

Universal Proto-Board PCB 4cm x
6 cm

QTY 1

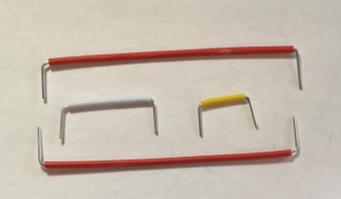
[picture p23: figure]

4 | SeeedStudio XAIO RP2040 with Included male headers | QTY 1 | 5 | 24 Gauge Wire or Protoboard Jumper Wires | 20 cm | 6 | M2 x 6 mm Self Tapping Screws | QTY 8

## MAKER GUIDE

Files available at https://github.com/makersmakingchange/Birch-Mini-Joystick | Page 11 of 31
10 | Birch Inner Disk | QTY 1 | 11 | Birch Enclosure
Bottom | QTY 1 | 12 | Birch Enclosure
Top | QTY 1

### Required Tools

- Flush Cutters
- Wire Strippers
- Soldering Iron
- Philips Head Screwdriver

### Required Personal Protective Equipment (PPE)

- Safety goggles

## MAKER GUIDE

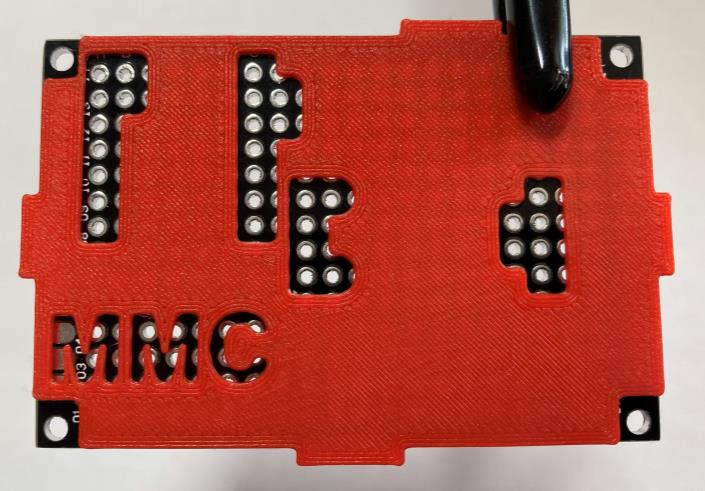
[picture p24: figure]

Files available at https://github.com/makersmakingchange/Birch-Mini-Joystick | Page 12 of 31

### Joystick Assembly

Step 1: Position the overlay
Place the 3D printed overlay on the protoboard.

Ensure the text “MMC” is in the same orientation as the text on the protoboard.

Step 2: Position microcontroller headers Place the two 7 pin male headers on the protoboard through the overlay from the top and place the XIAO microcontroller board on the headers.

Ensure the USB port on the XIAO is oriented towards the nearest edge on the protoboard.

3

4

9

## MAKER GUIDE

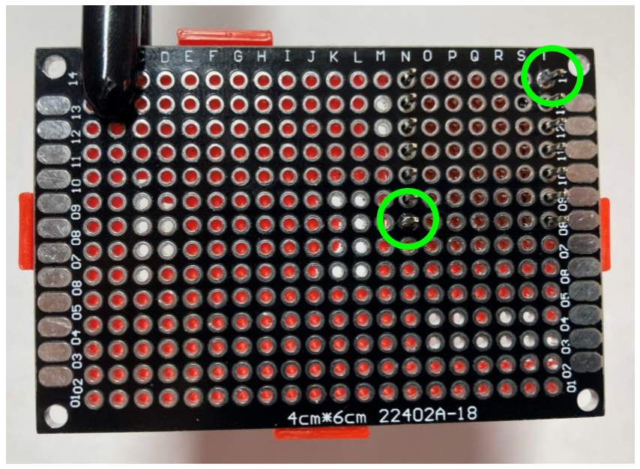
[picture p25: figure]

Files available at https://github.com/makersmakingchange/Birch-Mini-Joystick | Page 13 of 31
Step 3: Solder two header pins to board Solder one pin on each of the headers to the protoboard, ensuring the XIAO
microcontroller board
remains flat and straight.

Note: the header pins from the XIAO board should be
located at positions N08 – N14 and T08 – T14 (from
below).
(This only applies if the
numbering on your board
matches the photo)
Step 4: Solder remaining header pins to board Solder the remaining pins
from the XIAO board to the protoboard.

## MAKER GUIDE

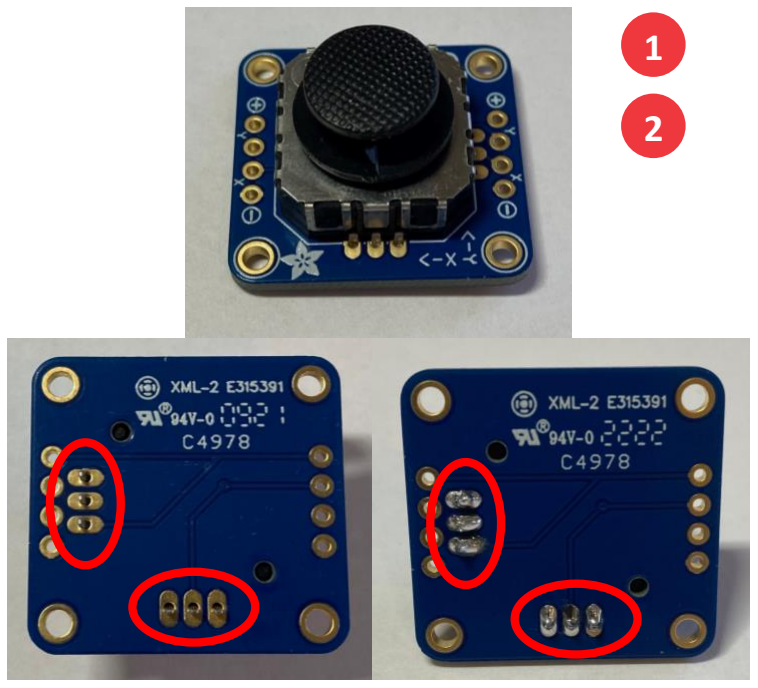
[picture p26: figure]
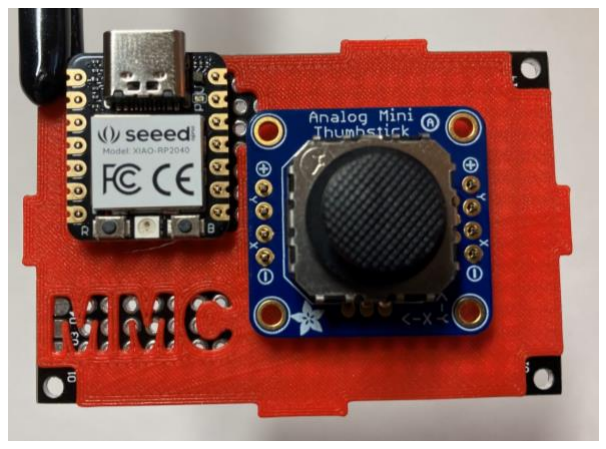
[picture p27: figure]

Files available at https://github.com/makersmakingchange/Birch-Mini-Joystick | Page 14 of 31
Step 5: Solder joystick to breakout board Insert the mini 2-axis analog thumbstick into the breakout board.

Solder the 6 pins, shown circled in red.

Step 6: Position joystick headers
Place the two 4 pin male headers on the protoboard through the overlay and place the joystick breakout board on the headers. If you have an 8 pin male header, gently break apart into two 4 pin headers, and then place headers onto the protoboard.

Ensure the breakout board is text side up and the text is in the same orientation as the text on the overlay.

## MAKER GUIDE

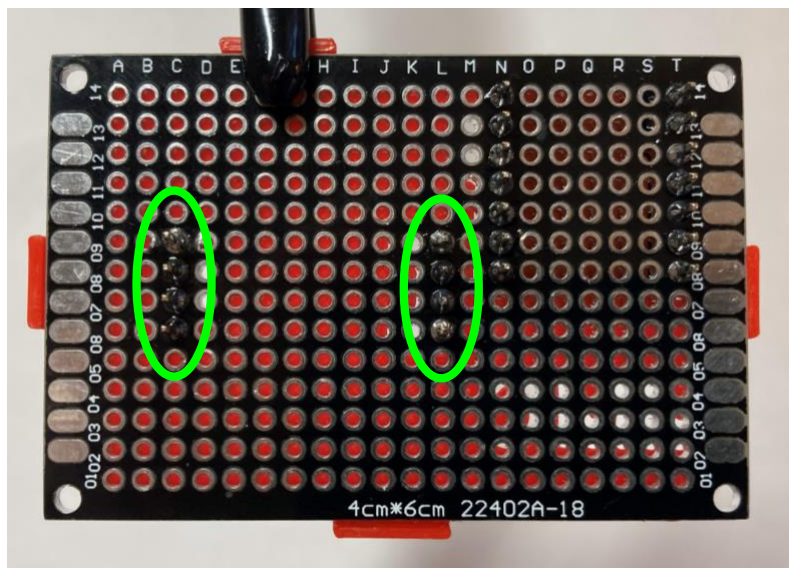
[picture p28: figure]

Files available at https://github.com/makersmakingchange/Birch-Mini-Joystick | Page 15 of 31
Step 7: Solder two header pins to board Solder one pin on each of the headers to the joystick
breakout board, ensuring the board remains flat and
straight.

Note: the header pins from the joystick breakout board should be located at positions C06 -C09 and L06 – L09 (from
below).
(This only applies if the
numbering on your board
matches the photo)
Step 8: Solder remaining header pins to board Solder the remaining pins from
the joystick breakout board to
the protoboard.

## MAKER GUIDE

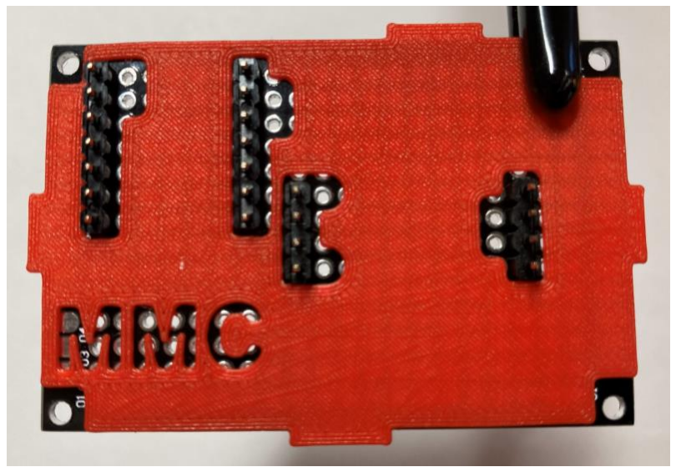
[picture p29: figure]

Files available at https://github.com/makersmakingchange/Birch-Mini-Joystick | Page 16 of 31
Step 9: Remove joystick and microcontroller Flip the board around and
remove the joystick breakout
board and the XIAO board from
the headers.

Wiring
For the next steps, this is the overall wiring diagram.
Seeed XIAO baord | Joystick breakout board
3v3 | +
GND | -
D0 | Y
D1 | X

## MAKER GUIDE

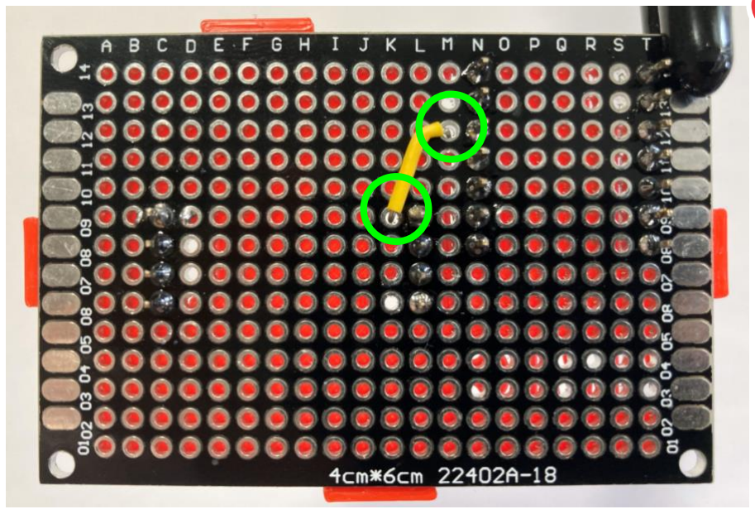
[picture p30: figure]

Files available at https://github.com/makersmakingchange/Birch-Mini-Joystick | Page 17 of 31
Step 10: Position first wire Insert a wire from hole
M12 to hole K09.

NOTE: All hole positions
are in reference to the
bottom of the board.

If the numbers and
letters on your
protoboard don’t match
this photo go from the
holes next to: Joystick
board, right header, top
pin TO XIAO board, left
header, 3rd pin from top.
Step 11: Solder first wire Solder the wire in place
and create solder
bridges from the wire
ends to the adjacent
pins. From M12 to N12,
from K09 to L09.

If the numbers and
letters on your
protoboard don’t match
this photo, go from your
new wire to the pin
directly to the right.

5

## MAKER GUIDE

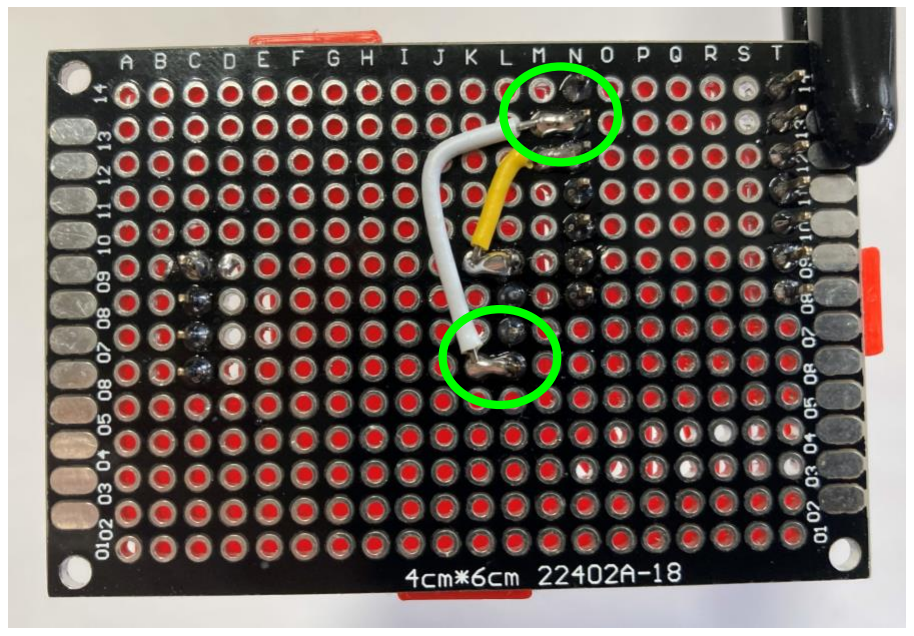
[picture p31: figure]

Files available at https://github.com/makersmakingchange/Birch-Mini-Joystick | Page 18 of 31
Step 12: Position and solder second wire Insert a wire from M13
to K06.

Solder the wire in place
and create solder
bridges from the wire
ends to the adjacent
pins. From M13 to N13
and from K06 to L06.

If the numbers and
letters don’t match this
photo go from the holes
to the left of: Joystick
board, right header,
bottom pin TO XIAO
board, left header, 2nd
pin from top.
Step 13: Position and solder third wire Insert a wire from S14 to
D08.

Solder the wire in place
and create solder
bridges from the wire
ends to the adjacent
pins. From S14 to T14
and from D08 to C08.

If the numbers and
letters don’t match this
photo go from the holes
next to: Joystick board,
left header, 2nd pin from
top TO XIAO board, right
header, top pin.

## MAKER GUIDE

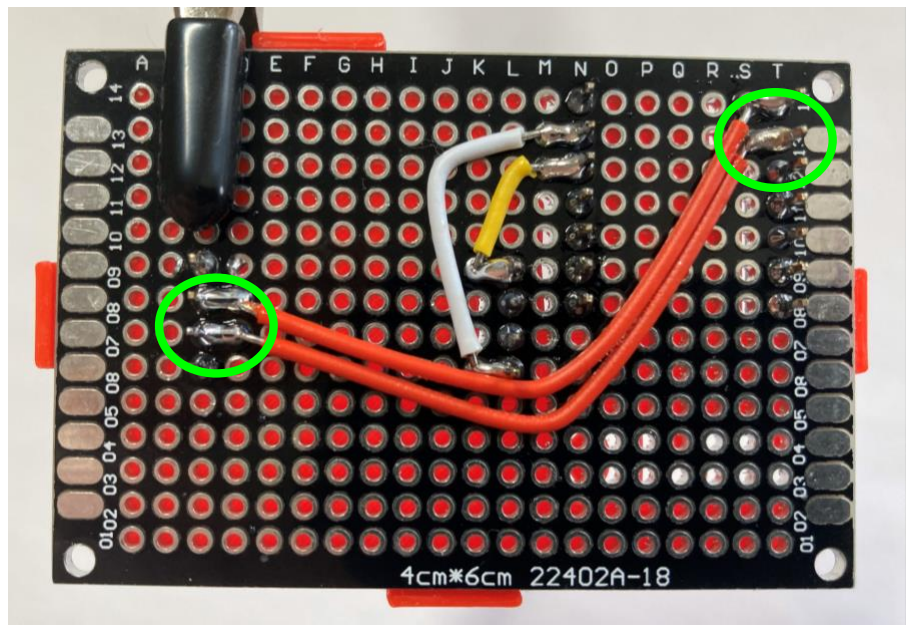
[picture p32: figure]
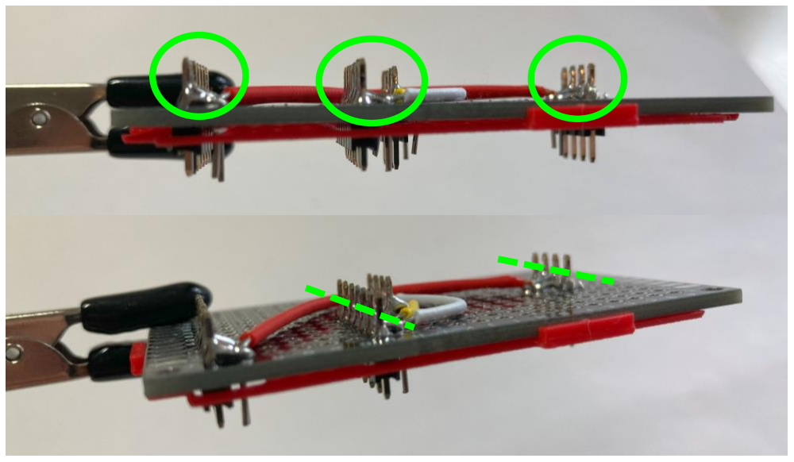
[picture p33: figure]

Files available at https://github.com/makersmakingchange/Birch-Mini-Joystick | Page 19 of 31
Step 14: Position and solder fourth wire Insert a wire from S13 to
D07.

Solder the wire in place
and create solder
bridges from the wire
ends to the adjacent
pins. From S13 to T13
and from D07 to C07.

If the numbers and
letters don’t match this
photo go from the holes
next to: Joystick board,
left header, 3rd pin from
top TO XIAO board, right
header, 2nd pin from top.
Step 15: Trim pins on the bottom of the board On the bottom of
the board, trim
the header pins
for both the
joystick board and
the XIAO board, as
shown circled in
green.

## MAKER GUIDE

Files available at https://github.com/makersmakingchange/Birch-Mini-Joystick | Page 20 of 31
Step 16: Trim excess wire on the top of the board On the top of the
board, trim the
extra length from
the jumper wires,
as shown circled
in green.

Do no trim the
male headers on
the top of the
board.

Below is how the board should look once the wires and bottoms of headers are trimmed.

## MAKER GUIDE

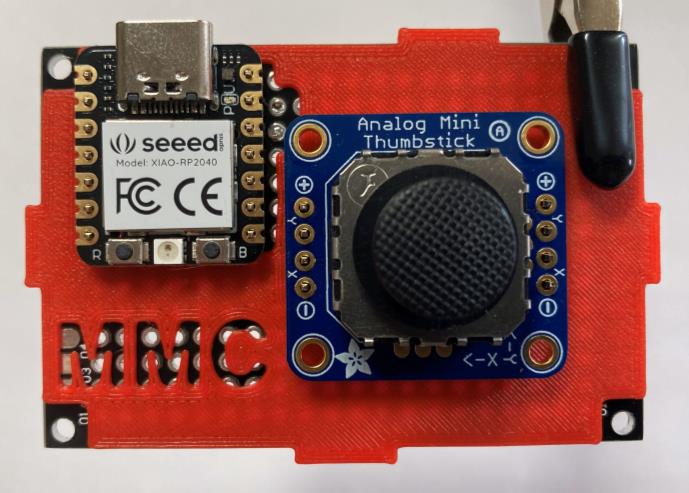
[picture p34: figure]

Files available at https://github.com/makersmakingchange/Birch-Mini-Joystick | Page 21 of 31
Step 17: Position microcontroller and joystick If you wish to re-use the 3D printed overlay you may remove it, or it may be left on.

Place the XIAO microcontroller board and the joystick breakout board onto their respective headers.

Ensure the USB port on the XIAO is oriented towards the nearest edge on the protoboard.

Ensure the text on the joystick board is in the same orientation as the text on the overlay/protoboard.

Step 17: Solder pins on microcontroller and joystick breakout board Solder the XIAO
microcontroller board and
the joystick breakout
board to their headers.

Ensure the boards stay
flat while soldering.

## MAKER GUIDE

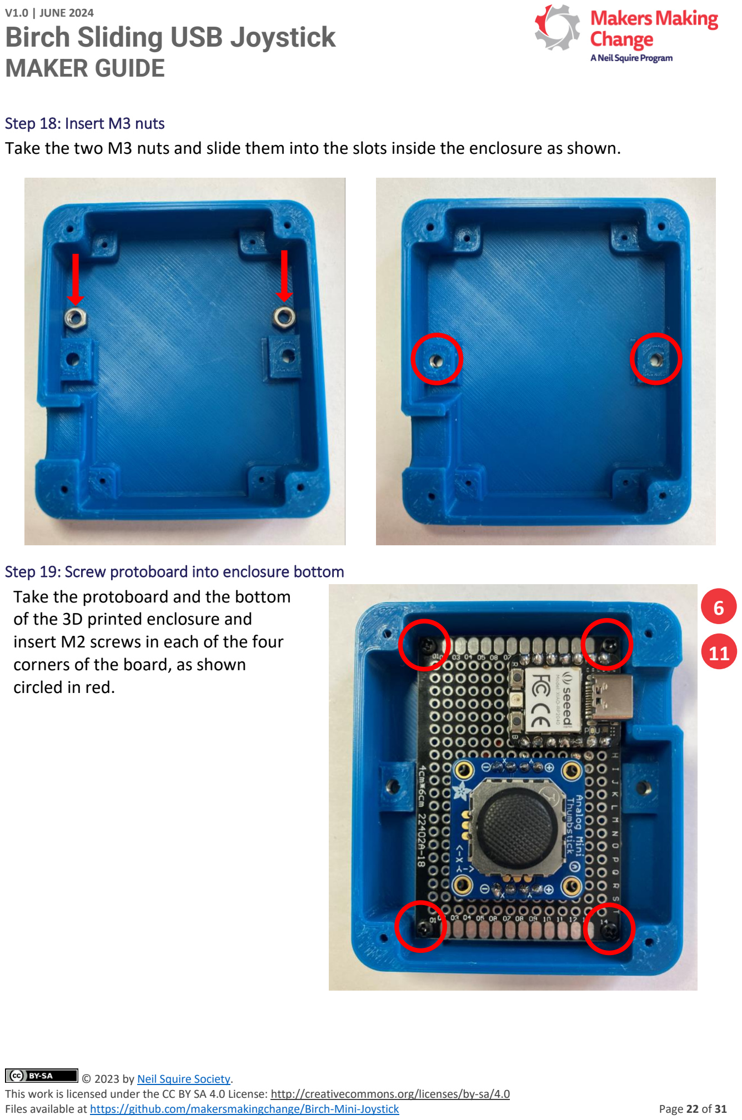
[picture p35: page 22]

Files available at https://github.com/makersmakingchange/Birch-Mini-Joystick | Page 22 of 31
Step 18: Insert M3 nuts
Take the two M3 nuts and slide them into the slots inside the enclosure as shown.
Step 19: Screw protoboard into enclosure bottom Take the protoboard and the bottom
of the 3D printed enclosure and
insert M2 screws in each of the four corners of the board, as shown circled in red.

6

11

## MAKER GUIDE

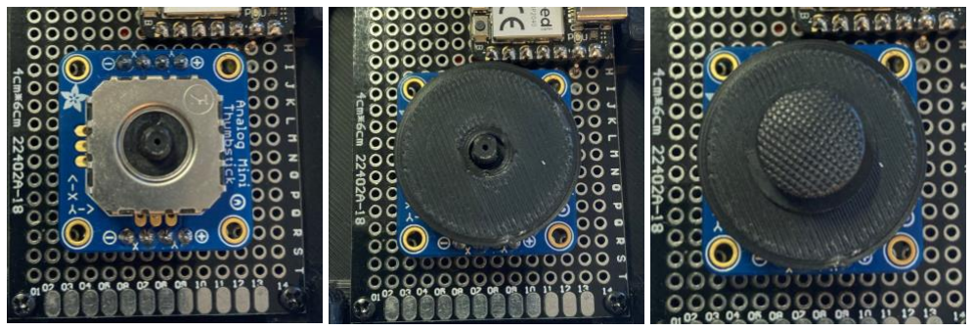
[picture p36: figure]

Files available at https://github.com/makersmakingchange/Birch-Mini-Joystick | Page 23 of 31
Step 20: Position inner disk Remove the
joystick topper.

Place the 3D
printed inner disk
on the joystick,
around the
joystick post.

Replace joystick
topper.

Note: if the joystick is difficult to move after this step, sand down the inner cover disk so it is smooth and does not have bumps or zits.

Step 21: Position enclosure top
Place the 3D printed enclosure lid on top of the enclosure base.

10

12

## MAKER GUIDE

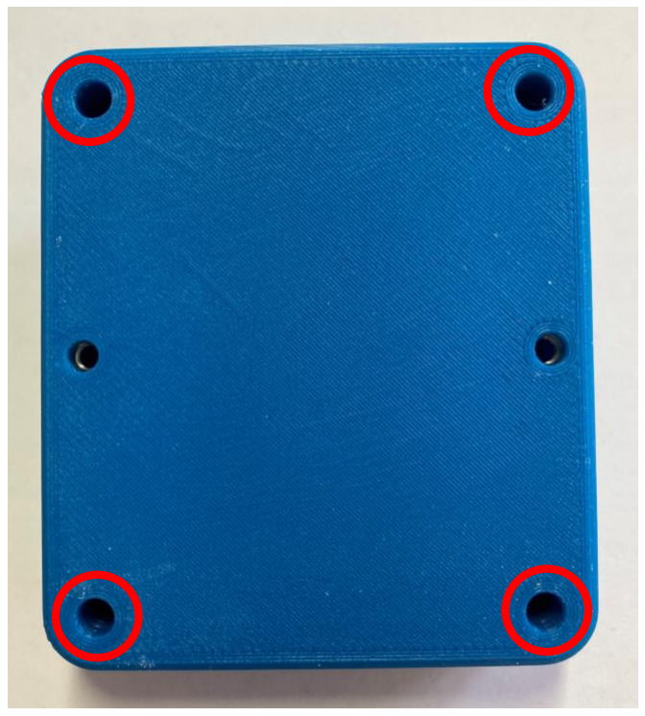
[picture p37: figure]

Files available at https://github.com/makersmakingchange/Birch-Mini-Joystick | Page 24 of 31
Step 22: Screw enclosure together
Flip the joystick around and insert an M2 screw into each of the 4 screw holes circled in red and tighten them.
Step 23: Plug in USB-C cable Plug the USB C cable into
the joystick, and proceed
to programming the
joystick.

6

8

## MAKER GUIDE

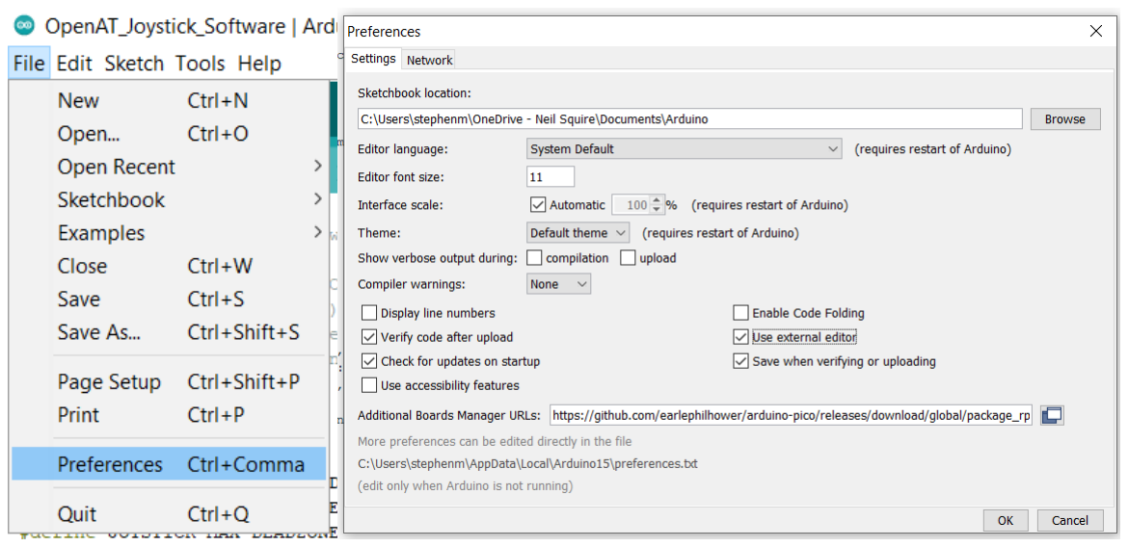
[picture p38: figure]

Files available at https://github.com/makersmakingchange/Birch-Mini-Joystick | Page 25 of 31

### Programming instructions

1. Setup Arduino IDE
1.1. Download Arduino IDE for your operating system at https://www.arduino.cc/en/software
1.2. Install Arduino IDE
2. Setup Core
2.1. Open Arduino IDE
2.2. Click on File -> Preferences
2.3. Locate the text field that says Additional Boards Manager URLs beside it.
2.4. Copy and paste the following link into the field as a new line: https://github.com/earlephilhower/arduino-pico/releases/download/global/package_rp2040_index.json (https://github.com/earlephilhower/arduino-pico/releases/download/global/package_rp2040_index.json)
2.5. Click on OK
2.6. Restart the Arduino IDE
2.7. Open the Boards Manager option from the Tools-> Board-> Boards Manager..., search for “Seeed Xiao” and select the package called “Raspberry Pi Pico/RP2040” by Earle F. Philhower, III

## MAKER GUIDE

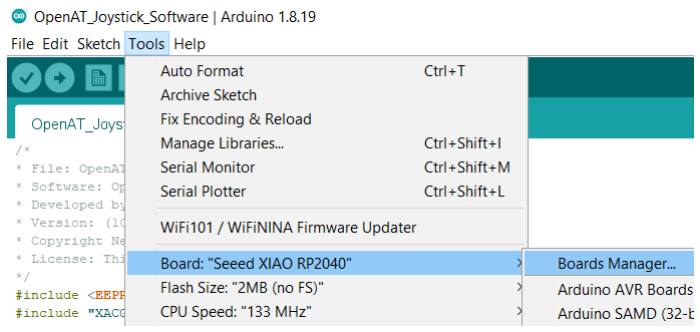
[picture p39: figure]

Files available at https://github.com/makersmakingchange/Birch-Mini-Joystick | Page 26 of 31
2.8. Select Seeed XIAO RP2040 from Tools -> Board -> Raspberry Pi RP2040 Boards menu.
2.9. Click on Tools -> USB Stack and select Adafruit TinyUSB

More Information: https://wiki.seeedstudio.com/XIAO-RP2040-with-Arduino/

3. Upload the Code to the joystick

## MAKER GUIDE

Files available at https://github.com/makersmakingchange/Birch-Mini-Joystick | Page 27 of 31
3.1. Open OpenAT_Joystick_Software_Birch.ino with Open Arduino ID.
3.2. Select Seeed XIAO RP2040 from Tools -> Board -> Raspberry Pi RP2040 Boards menu.
3.3. Connect the joystick using the USB cable to the computer.
3.4. Select the correct port from Tools -> Port menu.
3.5. Verify and upload the code.

## MAKER GUIDE

Files available at https://github.com/makersmakingchange/Birch-Mini-Joystick | Page 28 of 31

### Testing

1. Connect the joystick using the USB C cable to the computer.
2. If using Windows, open “Set up USB Game Controllers” from the Control Panel. You can find this by searching your computer in the search bar next to the Windows icon.
3. Ensure that the joystick is registered as a game controller and select your joystick from the list and go to “Properties”.
4. Move your joystick and observe the movement of the cross hatch in the “Axes” window. Ensure it moves in the proper directions when you move the joystick (the arrow points in the up direction). If not, open the joystick and check your connections.

## MAKER GUIDE

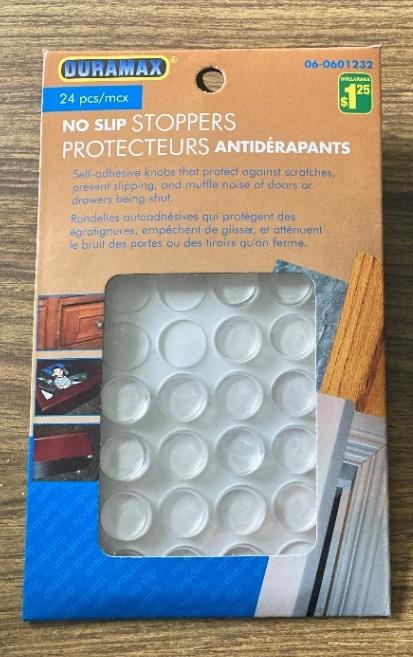
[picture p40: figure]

Files available at https://github.com/makersmakingchange/Birch-Mini-Joystick | Page 29 of 31

### Optional – Mounting

Table Top Mounting – Non-Slip Pads If using the joystick on a tabletop, and height of
the joystick is not a
concern, nonslip pads can
be added in each of the
four corners on the
bottom, as shown.

Table Top Mounting – Hook and Loop Fastener If using the joystick on a
tabletop or other surface
with hook and loop
fasteners, such as Velcro, stick the hook side (rough side) to the joystick and the loop side (soft side) to the surface to mount to.

## MAKER GUIDE

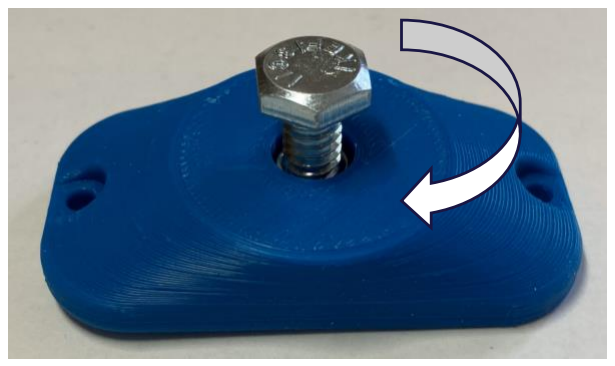
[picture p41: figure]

Files available at https://github.com/makersmakingchange/Birch-Mini-Joystick | Page 30 of 31

Camera Mount
To mount the joystick on a camera mount, the optional Joystick Camera Mount Adapter can be used.
Step 1

Flip the camera mount adapter around to reveal the recess with small slots.

Ensure all supports are removed from the 3D print.

Step 2

Insert the tee nut, lining up the barbs with the small slots in the 3D print.

Step 3

Flip the part around and screw in a ¼-20 hex bolt.

## MAKER GUIDE

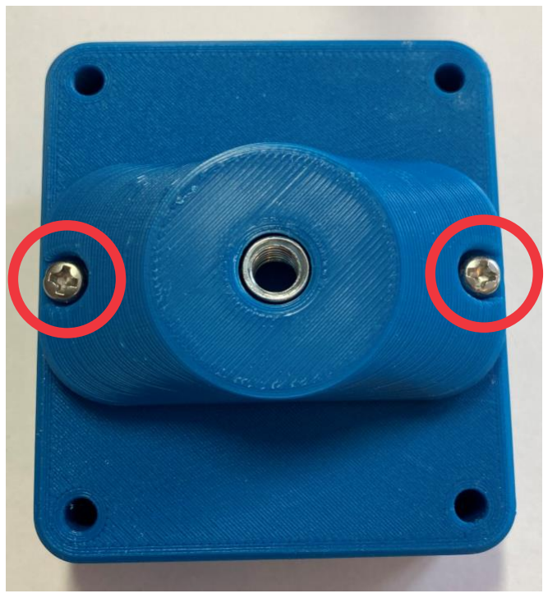
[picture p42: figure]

Files available at https://github.com/makersmakingchange/Birch-Mini-Joystick | Page 31 of 31
Step 4

Tighten the bolt until the tee nut is seated down as far as possible.

(Alternatively, if you do not have acces to a bolt, the tee nut may be press fit as long as it sits flush with the 3D print.)

Step 5

Using 2 M3 screws, screw the camera mount adapter to the bottom of the joystick in the two middle holes.

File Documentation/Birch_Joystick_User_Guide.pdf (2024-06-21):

V1.0 | JUNE 2024

## Birch Sliding USB Joystick

## USER QUICK GUIDE

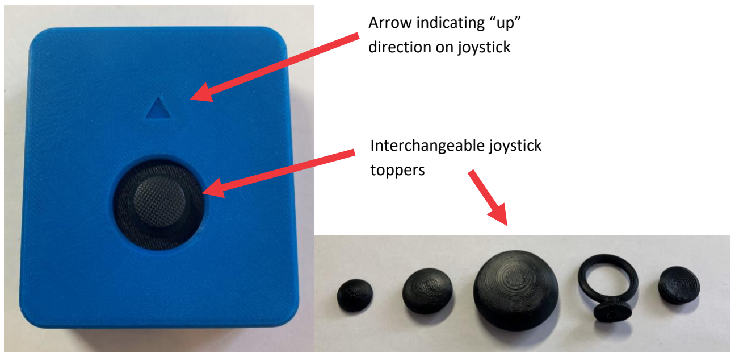
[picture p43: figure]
Arrow indicating “up” direction on joystick; Interchangeable joystick toppers
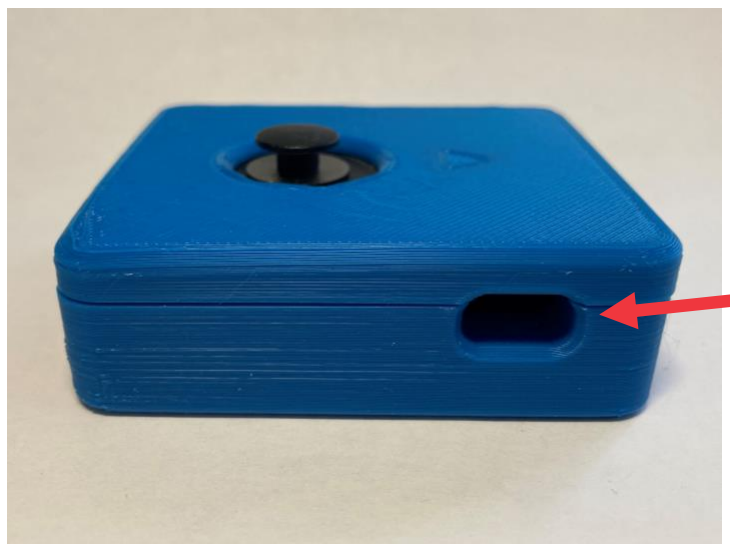
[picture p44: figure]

© 2023 by Neil Squire. (https://neilsquire.ca/)
This work is licensed under the CC BY SA 4.0 License: http://creativecommons.org/licenses/by-sa/4.0
Files available at https://github.com/makersmakingchange/Birch-Mini-Joystick | Page 1 of 6

### Introduction

The Birch Sliding USB Joystick is a small USB gaming joystick that moves in a sliding motion instead of the typical pivoting motion of a joystick or thumbstick. It has a relatively small range of motion and a moderate force required. It plugs into USB and can be used to play games with the Xbox Adaptive Controller (XAC).

### Features

USB Port
This is where the USB-C cable will plug into the joystick.

USB-C port

## USER QUICK GUIDE

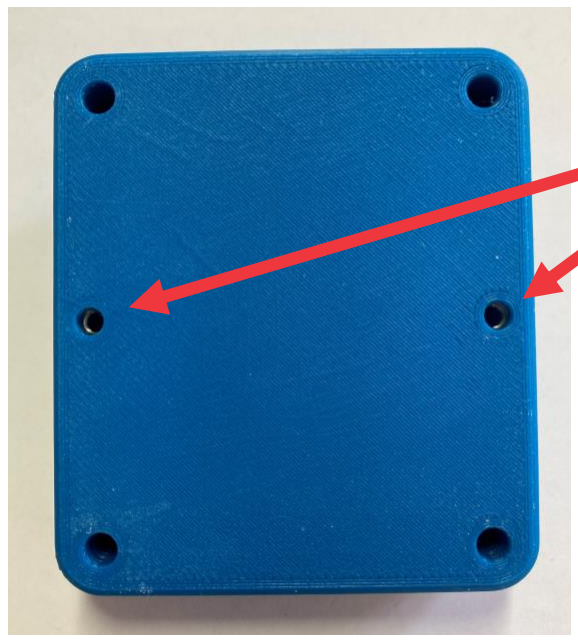
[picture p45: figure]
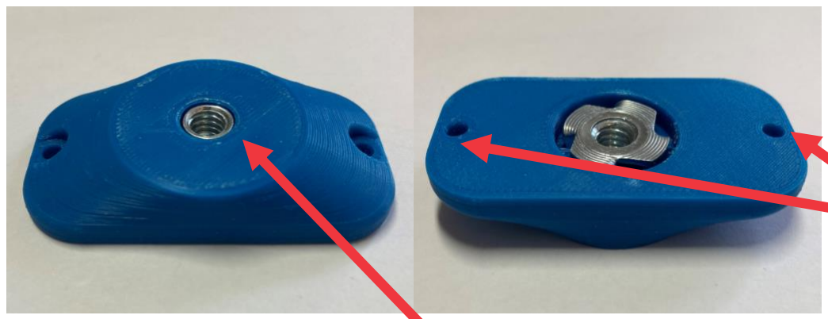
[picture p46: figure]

Files available at https://github.com/makersmakingchange/Birch-Mini-Joystick | Page 2 of 6

Mounting holes

Joystick Camera Mount Adapter
The Joystick Camera Mount Adapter allows the joystick to be mounted using a ¼-20 thread which is standard for camera mounts.

Screw holes for mount
adapters

Screw holes to attach
to joystick

¼-20 thread for camera mount

## USER QUICK GUIDE

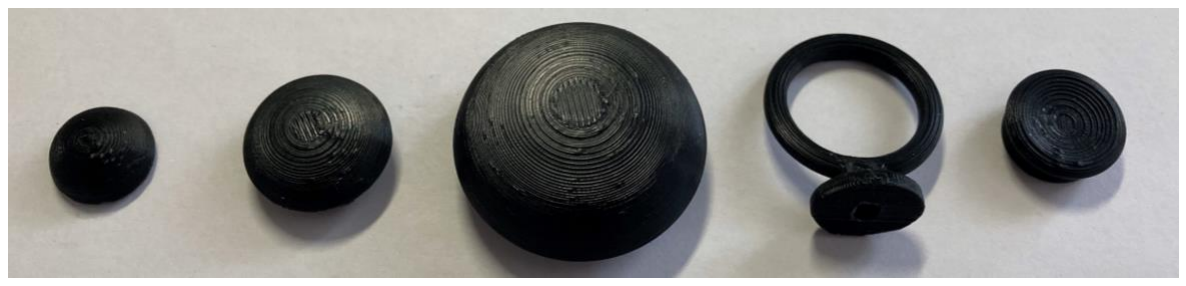
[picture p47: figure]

Files available at https://github.com/makersmakingchange/Birch-Mini-Joystick | Page 3 of 6

### Usage

Using the Joystick
1. Plug a USB-C to USB-A cable into the USB-C port on the joystick as shown above.
2. Plug the USB-A end of the cable into the host device (such as the Xbox Adaptive Controller).
3. Wait for joystick to initialize, approximately 15 seconds.
4. Ensure the arrow on the joystick is pointing in the “up” direction, away from the user.
5. Mount the device if needed (see below).
6. Move joystick as you would with a standard controller.

Compatibility
Compatible with the Xbox Adaptive Controller (XAC). May be compatible directly plugged into PC for some games.

This joystick is plug and play with the XAC and with PC, however will need additional switches for use without the XAC. Open source software such as Vjoy (https://github.com/shauleiz/vJoy) and Joystick Gremlin (http://whitemagic.github.io/JoystickGremlin/) can be used to combine switch inputs with the joystick.

Changing the Joystick Topper
There are a variety of toppers that can be 3D printed for this joystick, shown below.

To use them:

1. Remove the original joystick topper by pulling it off, revealing a small peg underneath
2. Take the 3D printed topper, check that it is in the correct orientation and press it onto the joystick. The fit should be snug.

## USER QUICK GUIDE

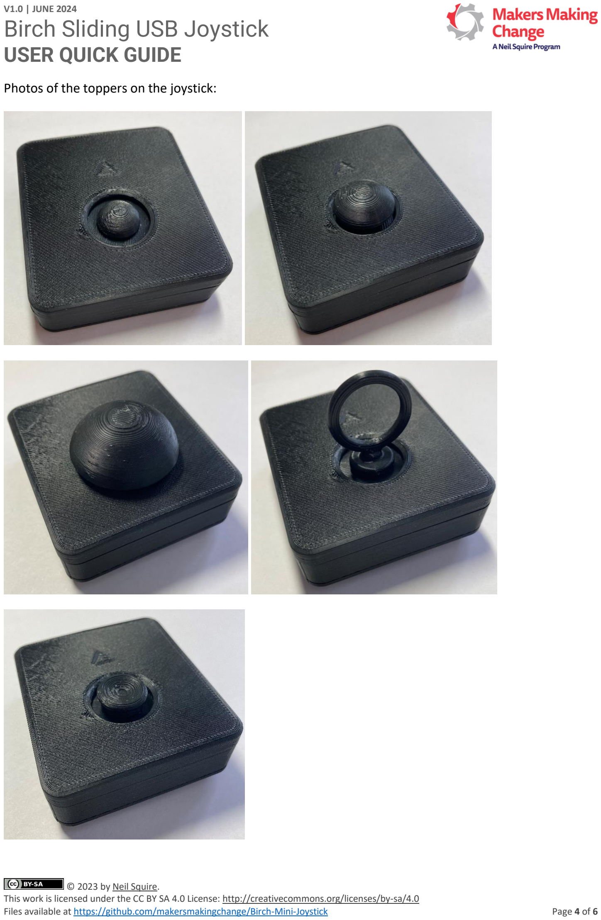
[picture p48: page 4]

Files available at https://github.com/makersmakingchange/Birch-Mini-Joystick | Page 4 of 6

Photos of the toppers on the joystick:

## USER QUICK GUIDE

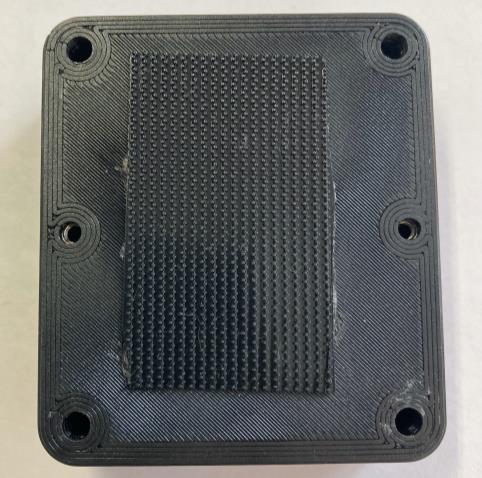
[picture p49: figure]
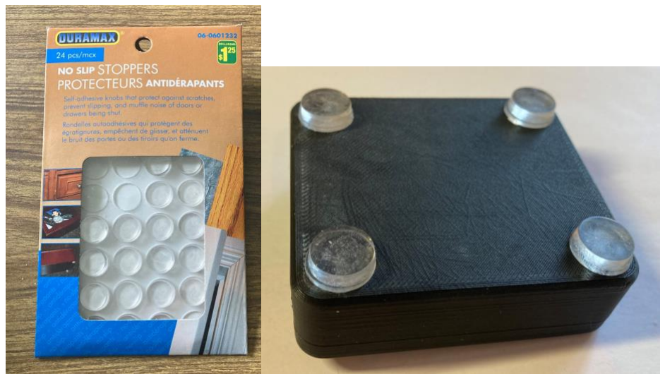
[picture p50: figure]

Files available at https://github.com/makersmakingchange/Birch-Mini-Joystick | Page 5 of 6

Mounting the Joystick

Tabletop – Hook and Loop Fastener
One way the joystick can be mounted, is on a tabletop or other surface such as a lap tray, and fastened using a hook and loop fastener such as Velcro.

Typically, best practice is to stick the side with the loops (the softer side) to the tabletop or other surface, and to stick the side with the hooks (rough side) to the joystick.

Tabletop – Non-slip pads
Another way the joystick can be use on the tabletop is by using a non slip material, such as the no slip stoppers shown below, or a non slip material such as Dycem.

¼-20 Threaded Camera Mount
Another way the joystick can be mounted, is by using a mount with a ¼-20 thread on the end, such as a commercially available camera mount. To mount the joystick on a ¼-20 thread, the Camera Mount Adapter is used. The assembly for this Camera Mount Adapter is found in the Assembly Guide.

## USER QUICK GUIDE

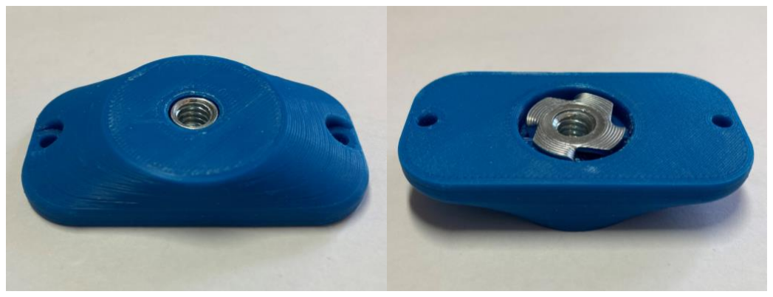
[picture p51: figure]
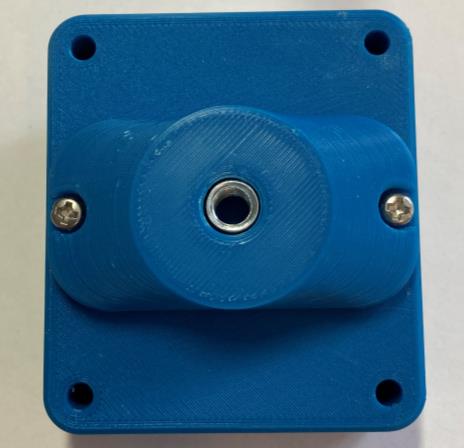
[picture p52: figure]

Files available at https://github.com/makersmakingchange/Birch-Mini-Joystick | Page 6 of 6

Camera Mount Adapter:

This is then screwed onto the bottom of the joystick, as shown below, using two M3 screws that are at least 10 mm long. Now, the joystick can be mounted on a mount with ¼-20 thread, such as a typical camera mount.

### Specifications

Total height (with default topper) | 2.4 cm
Enclosure height | 2.1 cm
Enclosure width | 6.0 cm
Enclosure length | 6.8 cm
Weight (without USB cable) | 48 grams
Weight (including 6ft USB cable) | 94 grams
Range of motion | ±2 mm
Activation force (to full deflection) | 115 grams of force

### Cleaning

The Birch Sliding USB Joystick can be wiped down with a damp cloth. Do not use hot water on this device or the plastic housing may warp. Do not submerge the device.

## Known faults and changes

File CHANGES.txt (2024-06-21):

------BIRCH MINI JOYSTICK------
           Changelog
===============================

Version 1.0	Date 13/06/2024
 - Renamed to Birch Sliding USB Joystick from Birch Mini Joystick
 - Seperated the USB and Analog versions
	- Analog version was redesigned and named Aspen Sliding Joystick
	- Analog version was cleaned out of this repository 
 - Assembly Guide, 3D Printing Guide, and Maker Checklist combined into Maker Guide
 - Removed Microsoft Word document changelog

Version 0.2 	Date 05/18/2023
 - Initial commit
 - Birch Mini joystick with 5 optional toppers and an optional camera mount adapter

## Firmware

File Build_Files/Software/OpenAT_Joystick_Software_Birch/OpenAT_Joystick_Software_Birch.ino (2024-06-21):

 /* 
* File: OpenAT_Joystick_Software_SlidingThumbstick.ino
* Software: OpenAT Joystick - Sliding Analog Thumbstick
* Developed by: MakersMakingChange
* Version: (19 July 2023) 
  License: GPL v3

  Copyright (C) 2023 Neil Squire Society
  This program is free software: you can redistribute it and/or modify it under the terms of
  the GNU General Public License as published by the Free Software Foundation,
  either version 3 of the License, or (at your option) any later version.
  This program is distributed in the hope that it will be useful, but WITHOUT ANY WARRANTY;
  without even the implied warranty of MERCHANTABILITY or FITNESS FOR A PARTICULAR PURPOSE.
  See the GNU General Public License for more details.
  You should have received a copy of the GNU General Public License along with this program.
  If not, see <http://www.gnu.org/licenses/>
*/
#include <EEPROM.h>
#include "XACGamepad.h"

#define JOYSTICK_DEFAULT_DEADZONE_LEVEL      1              //Joystick deadzone
#define JOYSTICK_MIN_DEADZONE_LEVEL          2
#define JOYSTICK_MAX_DEADZONE_LEVEL          10
#define JOYSTICK_MAX_DEADZONE_VALUE          64             //Out of 127
#define JOYSTICK_MAX_VALUE                   127 
#define JOYSTICK_REACTION_TIME               50             //Minimum time between each action in ms

//Define model number and version number
#define JOYSTICK_MODEL                        1
#define JOYSTICK_VERSION                      0.1

//Define Joystick Analog pins
#define JOYSTICK_X_PIN                        A0
#define JOYSTICK_Y_PIN                        A1  


//*** EEPROM MEMORY***// - DO NOT CHANGE
#define EEPROM_modelNumber                     0            // int:0,1;
#define EEPROM_versionNumber                   2            // float:2,3,4,5; 
#define EEPROM_deadzoneLevel                   6            // int:6,7;

XACGamepad gamepad;                                    //Starts an instance of the USB gamepad object

//Declare joystick input variables 
int inputX;
int inputY;

int currentDeadzoneValue;

bool settingsEnabled = false;

//***API FUNCTIONS***// - DO NOT CHANGE
typedef void (*FunctionPointer)(bool, bool, String);      //Type definition for API function pointer

typedef struct {                                  //Type definition for API function list
  String endpoint;                                //Unique two character end point
  String code;                                    //Unique one character command code
  String parameter;                               //Parameter that is passed to function
  FunctionPointer function;                       //API function pointer
} _functionList;

// Declare individual API functions with command, parameter, and corresponding function
_functionList getModelNumberFunction =            {"MN", "0", "0", &getModelNumber};
_functionList getVersionNumberFunction =          {"VN", "0", "0", &getVersionNumber};
_functionList getJoystickDeadZoneFunction =       {"DZ", "0", "0", &getJoystickDeadZone};
_functionList setJoystickDeadZoneFunction =       {"DZ", "1", "",  &setJoystickDeadZone};

// Declare array of API functions
_functionList apiFunction[5] = {
  getModelNumberFunction,
  getVersionNumberFunction,
  getJoystickDeadZoneFunction,
  setJoystickDeadZoneFunction
};

//***MICROCONTROLLER AND PERIPHERAL CONFIGURATION***//
// Function   : setup 
// 
// Description: This function handles the initialization of variables, pins, methods, libraries. This function only runs once at powerup or reset.
// 
// Parameters :  void
// 
// Return     : void
//*********************************//
void setup() {
  // Begin HID gamepad 
  gamepad.begin();

  // Initialize EEPROM 
  EEPROM.begin(512);
  delay(10000);
  // Initialize Joystick 
  initJoystick();

  // Begin serial
  Serial.begin(115200);
}

void loop() {

    settingsEnabled=serialSettings(settingsEnabled); //Check to see if setting option is enabled
    readJoystick();
    delay(JOYSTICK_REACTION_TIME);
}

//*********************************//
// Joystick Functions
//*********************************//

//***INITIALIZE JOYSTICK FUNCTION***//
// Function   : initJoystick 
// 
// Description: This function initializes joystick as input.
//
// Parameters : void
// 
// Return     : void 
//****************************************//
void initJoystick()
{
  getJoystickDeadZone(true,false);                                          //Get joystick deadzone stored in memory                                      //Get joystick calibration points stored in flash memory 
}

//***READ JOYSTICK FUNCTION**//
// Function   : readJoystick
//
// Description: This function reads the current raw values of potentiometers, checks if values exceed deadband, and calculates
//              joystick movements. Outputs true if joystick should be moved.
//
// Parameters :  Void
//
// Return     : Void
//*********************************//

void readJoystick() {
    //Read analog raw value using ADC
    inputX = analogRead(JOYSTICK_X_PIN);
    inputY = analogRead(JOYSTICK_Y_PIN);

    //Map joystick x and y move values 
    int outputX = map(inputX, 0, 1023, -127, 127);
    int outputY = map(inputY, 0, 1023, -127, 127);

    double outputMag = calcMag(outputX, outputY);
    
    //Apply radial deadzone *********************************************************************
    if (outputMag<=currentDeadzoneValue) 
    {
      outputX = 0;
      outputY = 0;
    }
    
    //Perform joystick HID action 
    gamepadJoystickMove(outputX,outputY);
}


//***UPDATE JOYSTICK DEADZONE FUNCTION***//
// Function   : updateDeadzone 
// 
// Description: This function updates deadzone value based on deadzone level.
//
// Parameters :  inputDeadzoneLevel : int : The input deadzone level
// 
// Return     : void 
//****************************************//

void updateDeadzone(int inputDeadzoneLevel){
  if ((inputDeadzoneLevel >= JOYSTICK_MIN_DEADZONE_LEVEL) && (inputDeadzoneLevel <= JOYSTICK_MAX_DEADZONE_LEVEL)) {
    currentDeadzoneValue = int ((inputDeadzoneLevel*JOYSTICK_MAX_DEADZONE_VALUE)/JOYSTICK_MAX_DEADZONE_LEVEL);
    currentDeadzoneValue = constrain(currentDeadzoneValue, 0, JOYSTICK_MAX_DEADZONE_VALUE);
  }  
}


//***GAMEPAD BUTTON PRESS FUNCTION***//
// Function   : gamepadButtonPress 
// 
// Description: This function performs button press action.
//
// Parameters : int : buttonNumber
// 
// Return     : void 
//****************************************//
void gamepadButtonPress(int buttonNumber)
{
  //Serial.println("Button Press");
  if (buttonNumber >0 && buttonNumber <=8 )
  {
    gamepad.press(buttonNumber-1);
    gamepad.send();
  }
}

//***GAMEPAD BUTTON CLICK FUNCTION***//
// Function   : gamepadButtonClick
// 
// Description: This function performs button click action.
//
// Parameters : int : buttonNumber
// 
// Return     : void 
//****************************************//
void gamepadButtonClick(int buttonNumber)
{
  //Serial.println("Button click");
  if (buttonNumber >0 && buttonNumber <=8 )
  {
    gamepad.press(buttonNumber-1);
    gamepad.send();
    delay(JOYSTICK_REACTION_TIME);
    gamepadButtonRelease(buttonNumber);
  }

}

//***GAMEPAD BUTTON RELEASE FUNCTION***//
// Function   : gamepadButtonRelease 
// 
// Description: This function performs button release action.
//
// Parameters : int* : args
// 
// Return     : void 
//****************************************//
void gamepadButtonRelease(int buttonNumber)
{
  //Serial.println("Button Release");
  if (buttonNumber >0 && buttonNumber <=8){
    gamepad.release(buttonNumber-1);
    gamepad.send();
  }

}

//***GAMEPAD BUTTON RELEASE FUNCTION***//
// Function   : gamepadButtonReleaseAll 
// 
// Description: This function performs button release action.
//
// Parameters : void
// 
// Return     : void 
//****************************************//
void gamepadButtonReleaseAll()
{
  //Serial.println("Button Release");
  gamepad.releaseAll();
  gamepad.send();
}


//***PERFORM JOYSTICK MOVE FUNCTION***//
// Function   : gamepadJoystickMove 
// 
// Description: This function performs joystick move
//
// Parameters : int : x and y : The output gamepad x and y
// 
// Return     : void 
//****************************************//
void gamepadJoystickMove(int x, int y)
{
  gamepad.move(x, -y);
  gamepad.send();
}


//***SERIAL SETTINGS FUNCTION TO CHANGE SPEED AND COMMUNICATION MODE USING SOFTWARE***//
// Function   : serialSettings
//
// Description: This function confirms if serial settings should be enabled.
//              It returns true if it's in the settings mode and is waiting for a command.
//              It returns false if it's not in the settings mode or it needs to exit the settings mode.
//
// Parameters :  enabled : bool : The input flag
//
// Return     : bool
//*************************************************************************************//
bool serialSettings(bool enabled) {

  String commandString = "";
  bool settingsFlag = enabled;

  //Set the input parameter to the flag returned. This will help to detect that the settings actions should be performed.
  if (Serial.available() > 0)
  {
    //Check if serial has received or read input string and word "SETTINGS" is in input string.
    commandString = Serial.readString();
    if (settingsFlag == false && commandString == "SETTINGS") {
      //SETTING received
      //Set the return flag to true so settings actions can be performed in the next call to the function
      printResponseInt(true, true, true, 0, commandString, false, 0);
      settingsFlag = true;
    } else if (settingsFlag == true && commandString == "EXIT") {
      //EXIT Recieved
      //Set the return flag to false so settings actions can be exited
      printResponseInt(true, true, true, 0, commandString, false, 0);
      settingsFlag = false;
    } else if (settingsFlag == true && isValidCommandFormat(commandString)) { //Check if command's format is correct and it's in settings mode
      performCommand(commandString);                  //Sub function to process valid strings
      settingsFlag = false;
    } else {
      printResponseInt(true, true, false, 0, commandString, false, 0);
      settingsFlag = false;
    }
    Serial.flush();
  }
  return settingsFlag;
}
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

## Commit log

2023-05-16 Renamed files
    [Birch_Mini_Joystick-A_BOM.xlsx, Birch_Mini_Joystick-A_BOM_v0.2.xlsx, Birch_Mini_Joystick-U_BOM.xlsx, Birch_Mini_Joystick-U_BOM_v0.2.xlsx]
2024-02-23 Updated Assembly Guide
2024-06-21 v1.0.0 upload
    [Birch_Enclosure_Bottom v0.2.stl, Birch_Enclosure_Bottom.stl, Birch_Enclosure_Top v0.2.stl, Birch_Enclosure_Top.stl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]
